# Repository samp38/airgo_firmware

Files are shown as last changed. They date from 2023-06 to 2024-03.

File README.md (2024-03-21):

# airgo_firmware
[link to project](https://wikilab.myhumankit.org/index.php?title=Projets:Automatisation_Support_Joystick_Menton_Fauteuil_Roulant)

## Mode of operation
This setup mean to drive a retractable arm that hold a joystick needed to stir an electrical weelchair. The arm can be retracted/extended to its end positions or stopped inbetween. The system is composed of :
- a push button big enough to be actuated with the head. (temporary contact, normally open)
- an arduino mini pro (atmega328p in its 3.3v version preferably)
- a DC motor H-Bridge driver (DVR 8838) to drive the linear actuator that moves the arm
- the linear actuator itself, with en of course switches that autmatically open the power circuit when the it reaches its end of course positions

Once assembled, the system works as described :
- a long press will retract the arm
- a double press will extend the arm
- a simple press will stop the arm

The system works on 7.4 Li-Ion battery, but the arduino mini pro is powered by one cell only on its RAW input, to shunt the voltage regulator. You also have to remove the led on the arduino, so it won't draw current during deep sleep. With this setup, we're able to draw 5 uA in deep sleep mode. As the arduino mini pro doesn't have a usb2serial chip, you will have to [program it with an external programmer](https://www.instructables.com/How-to-Program-Arduino-Pro-Mini-Using-Arduino-UNO/) (arduino as isp, ftdi...).

## Firmware specifications
- smart push button with actions linked to different press types (short press, long press and double press)
- deep sleep, wake on external interrupt of the push button
- drive DC motor CW or CCW depending on state
- (optional) motor current monitoring via shunt resistor and avr ADC

## Hardware
- arduino mini pro 8Mhz
- motor driver DVR8838
- [Schematics here](./doc/schematics.pdf)
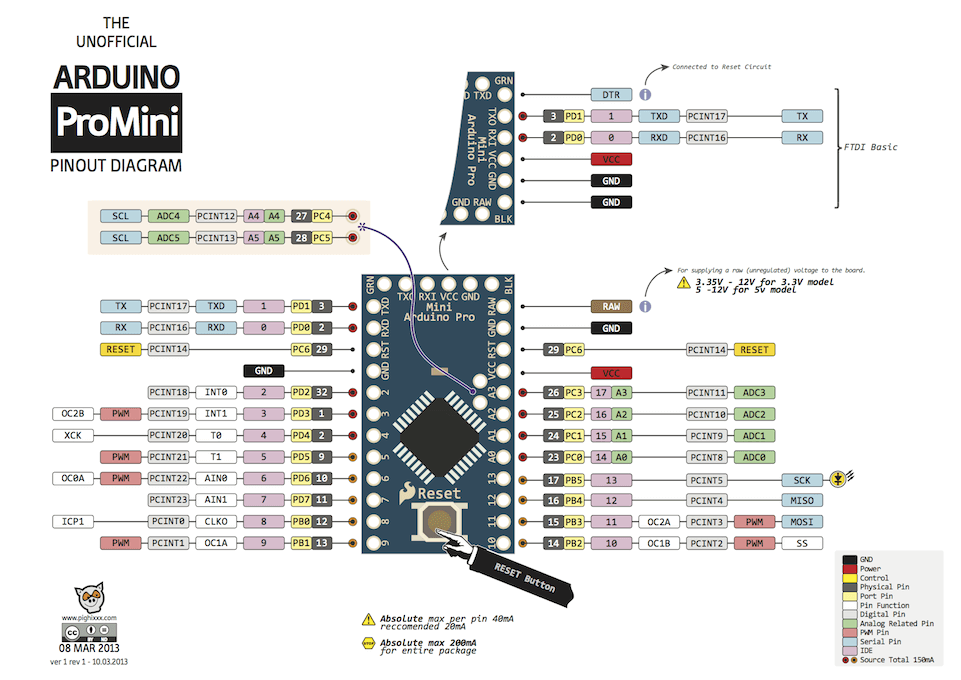
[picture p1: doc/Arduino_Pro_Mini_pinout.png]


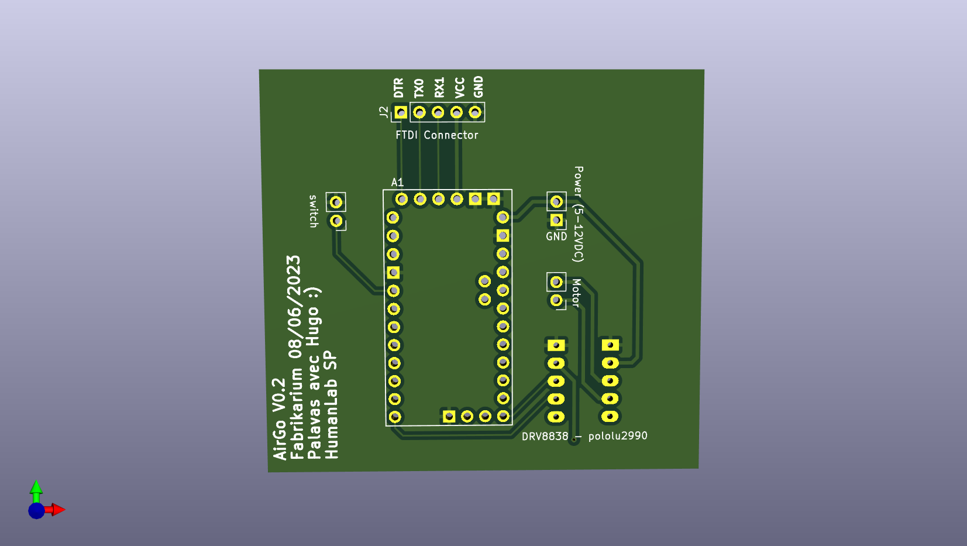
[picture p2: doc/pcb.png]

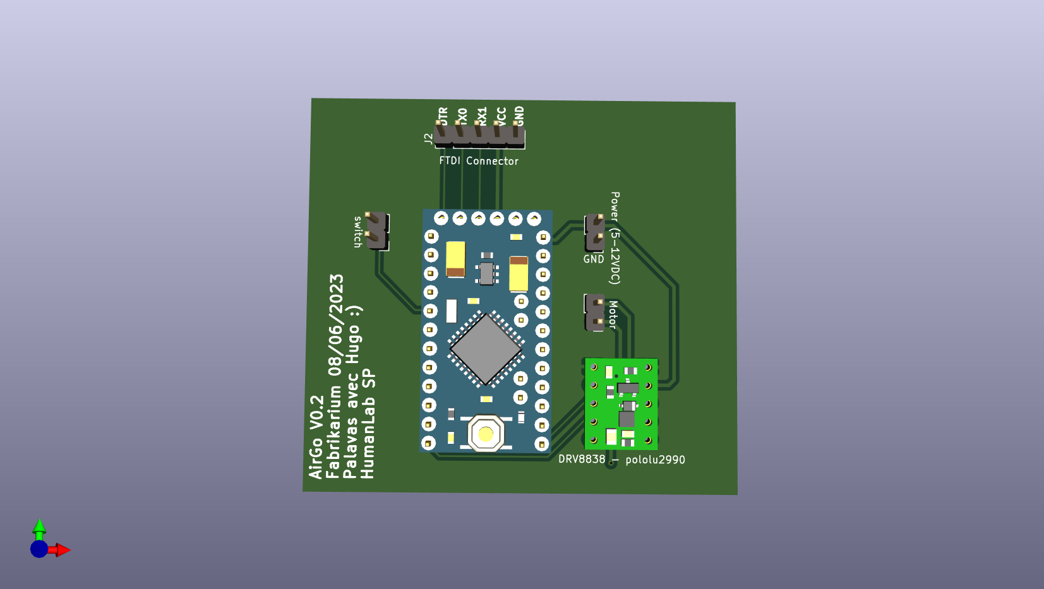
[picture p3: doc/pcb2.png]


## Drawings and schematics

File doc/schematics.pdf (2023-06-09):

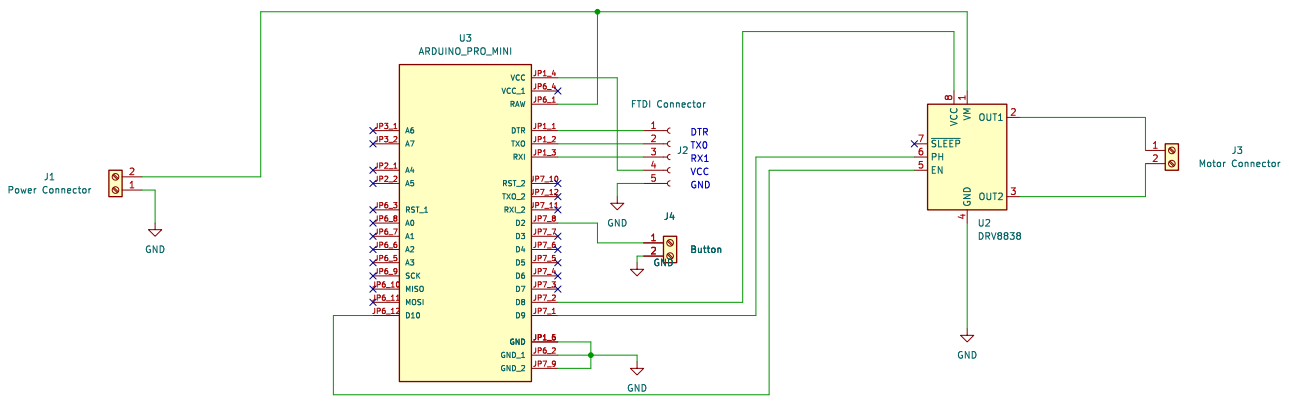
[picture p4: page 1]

J2 FTDI Connector GND GND

4 EN 5 PH 6 ~{SLEEP} 7 VCC

Id: 1/1 Title: File: AirGo.kicad_sch Sheet: /

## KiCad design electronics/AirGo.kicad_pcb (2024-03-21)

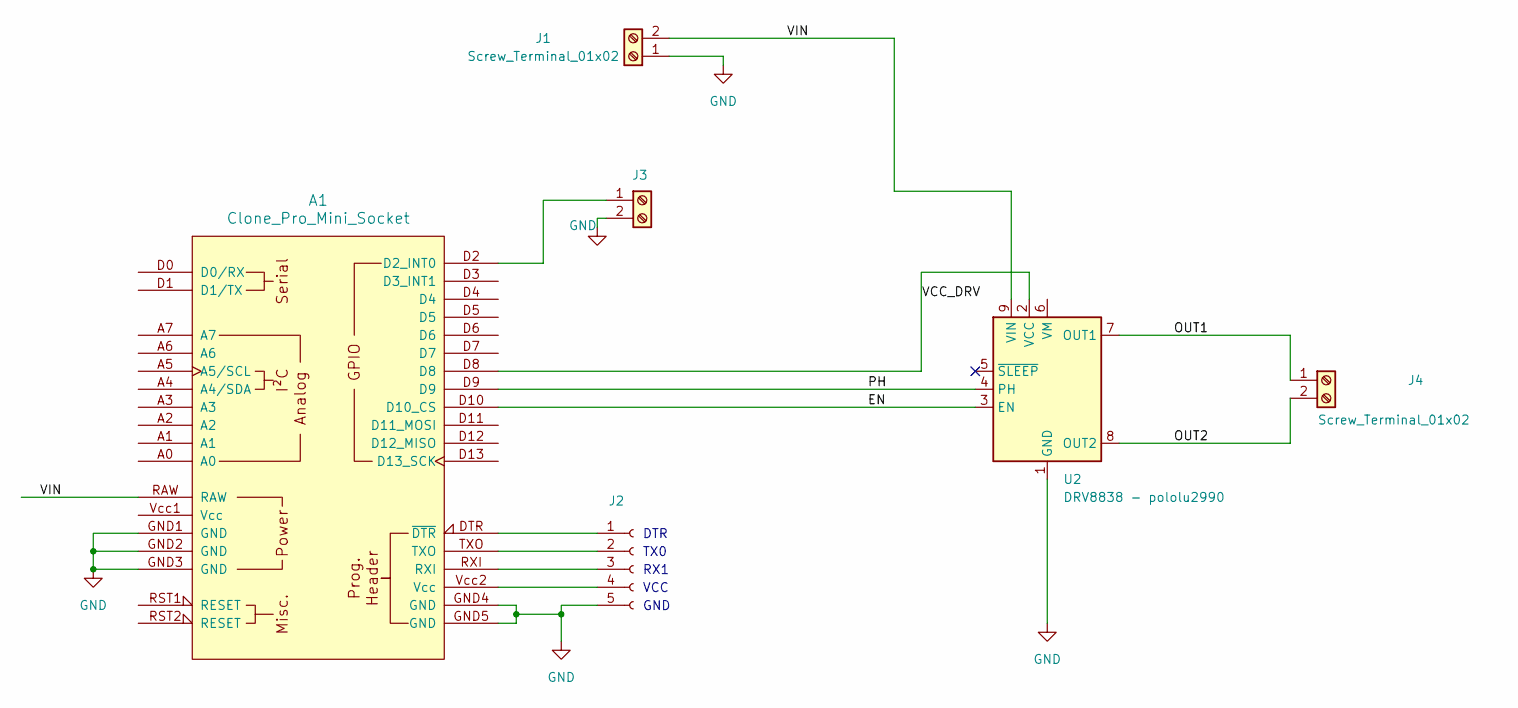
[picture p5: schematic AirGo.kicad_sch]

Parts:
A1: Clone_Pro_Mini_Socket
J1, J3, J4: Screw_Terminal_01x02; PinHeader_1x02_P2.54mm_Vertical
J2: Conn_01x05_Socket; PinHeader_1x05_P2.54mm_Vertical
U2: DRV8838 - pololu2990; DIP-10_W7.62mm_LongPads

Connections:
/EN: A1.D10 (D10_CS), U2.3 (EN)
/OUT1: J4.1, U2.7 (OUT1)
/OUT2: J4.2, U2.8 (OUT2)
/PH: A1.D9, U2.4 (PH)
/VCC_DRV: A1.D8, U2.2 (VCC)
/VIN: A1.RAW, J1.2, U2.9 (VIN)
GND: A1.GND1 (GND), A1.GND2 (GND), A1.GND3 (GND), A1.GND4 (GND), A1.GND5 (GND), J1.1, J2.5, J3.2, U2.1 (GND), U2.10 (GND)
unnamed: A1.D2 (D2_INT0), J3.1
unnamed: A1.DTR (~DTR), J2.1
unnamed: A1.TXO, J2.2
unnamed: A1.RXI, J2.3
unnamed: A1.Vcc2 (Vcc), J2.4

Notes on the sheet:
TX0
DTR
VCC
RX1
GND

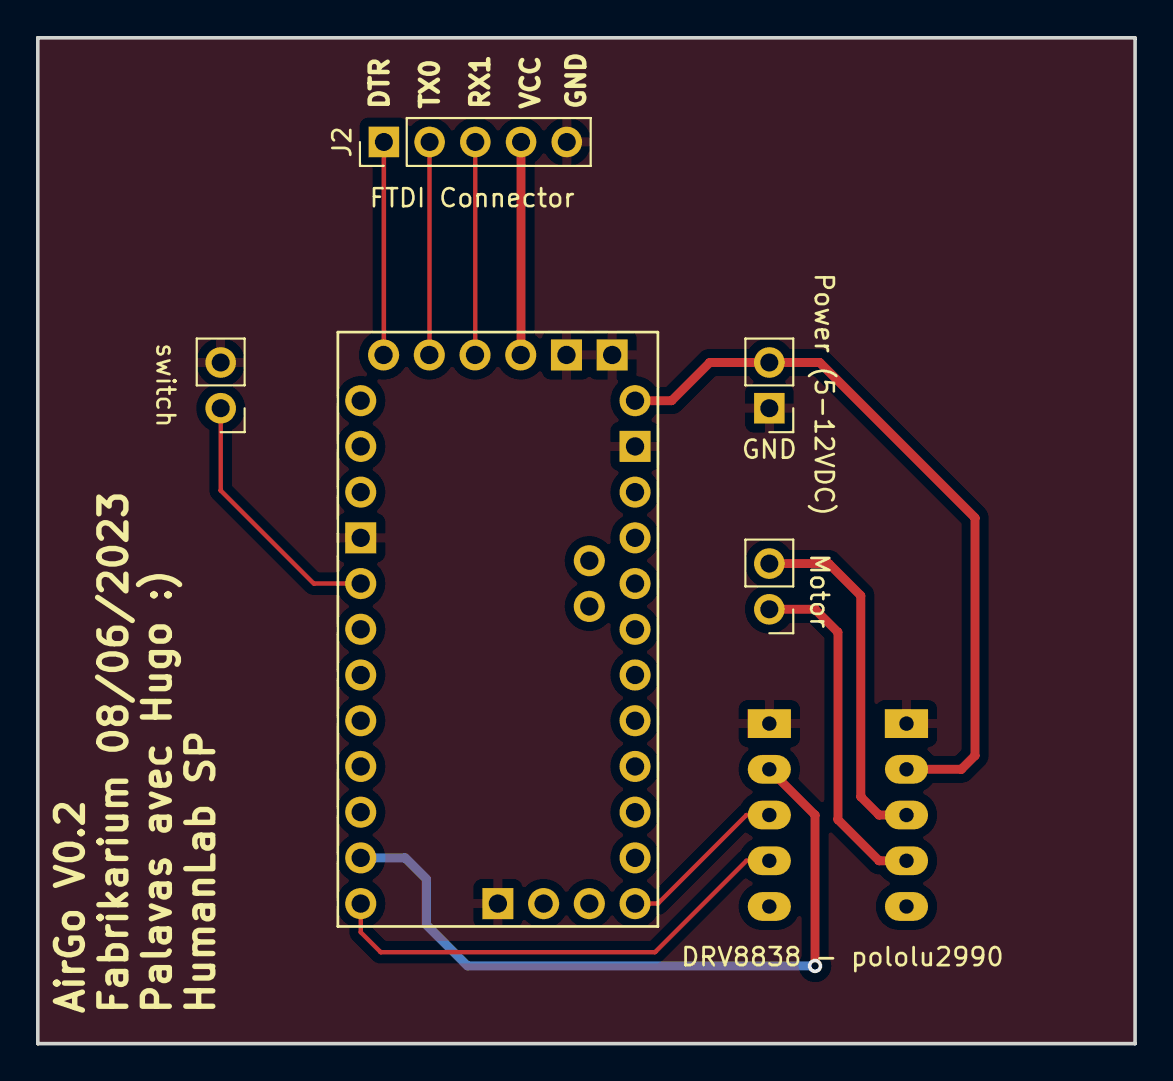
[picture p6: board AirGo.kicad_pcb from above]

Board: 2 copper layers, 61.0 x 55.9 mm, 6 parts (0 on the bottom side), 12 nets.

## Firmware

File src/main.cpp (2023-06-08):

#include "Arduino.h"
#include <EEPROM.h>
#include "bsp.h"
#include "LowPower.h"
#include "OneButton.h"

#define TIMER_SEC 15
#define DOUBLE_CLICK_MS 800
#define LONG_PRESS_MS 1000

// Globals
static volatile bool run_interrupt = 0;
static volatile unsigned int timer_count_sec;
unsigned long pressStartTime;

// Setup a new OneButton on pin PUSH_BUTTON_IN
// The 2. parameter activeLOW is true, because external wiring sets the button to LOW when pressed.
OneButton button(PUSH_BUTTON_IN, true);


void motor_stop() {
    digitalWrite(MOTOR_EN, LOW);
    digitalWrite(MOTOR_DIR, HIGH);
    digitalWrite(MOTOR_DRIVER_PW, LOW);
}

void motor_drive(float speed) {
    unsigned int abs_speed;
    // if speed == 0, stop motor
    if (speed == 0) {
        motor_stop();
        return;
    }

    // if speed is not 0, drive motor
    digitalWrite(MOTOR_DRIVER_PW, HIGH);
    if abs(speed > 100) {
        speed = 100;
    } else if (speed < -100)
    {
        speed = -100;
    }
    
    abs_speed = (unsigned int) (abs(speed) * 255./100.);
    
    if (speed > 0) {
        digitalWrite(MOTOR_DIR, HIGH);
    }
    else
    {
        digitalWrite(MOTOR_DIR, LOW);
    }
    analogWrite(MOTOR_EN, abs_speed);
}

void stop_timer() {
    TIMSK1 |= (0 << TOIE1);   // disable timer overflow interrupt
}

void start_timer(volatile unsigned int local_timer_count_sec = TIMER_SEC) {
    TCNT1 = 31250;   // preload timer
    timer_count_sec = local_timer_count_sec;
    TIMSK1 |= (1 << TOIE1);   // enable timer overflow interrupt
}

void trig_interrupt(){
    // run_interrupt = 1;
    button.tick(); // just call tick() to check the state.
}

// this function will be called when the button was pressed 1 time only.
void singleClick() {
    Serial.println("singleClick() detected.");
    start_timer(1);
    motor_drive(0);
} // singleClick

// this function will be called when the button was pressed 2 times in a short timeframe.
void doubleClick() {
    start_timer();
    Serial.println("doubleClick() detected.");
    Serial.println("extending");
    motor_drive(-100);
} // doubleClick

// this function will be called when the button was held down for 1 second or more.
void longPress() {
    start_timer();
    pressStartTime = millis() - LONG_PRESS_MS; // as set in setPressMs()
    // Serial.println("longPress()");
    Serial.println("retracting");
    motor_drive(100);
} // pressStart()


void setup() {
    Serial.begin(9600);
    noInterrupts(); 
    // Set pin modes
    pinMode(MOTOR_DIR, OUTPUT);
    pinMode(MOTOR_EN, OUTPUT);
    pinMode(MOTOR_DRIVER_PW, OUTPUT);
    pinMode(PUSH_BUTTON_IN, INPUT_PULLUP);

    // setup Timer1
    TCCR1A = 0;
    TCCR1B = 0;

    TCNT1 = 31250;   // preload timer
    TCCR1B |= (1 << CS12);    // 256 prescaler
    TIMSK1 |= (1 << TOIE1);   // enable timer overflow interrupt
    stop_timer();
    motor_stop();

    interrupts();   

    // stop motor
    motor_drive(0);

    // Attach interrupt
    attachInterrupt(digitalPinToInterrupt(PUSH_BUTTON_IN), trig_interrupt, FALLING);

    // button mngmt
    // link the xxxclick functions to be called on xxxclick event.
    button.attachClick(singleClick);
    button.attachDoubleClick(doubleClick);

    button.setClickMs(DOUBLE_CLICK_MS);
    button.setPressMs(LONG_PRESS_MS); // that is the time when LongPressStart is called
    button.attachLongPressStart(longPress);
    // button.attachLongPressStop(pressStop);
}

void loop() {
    button.tick();
}

ISR(TIMER1_OVF_vect)        // interrupt service routine every one second
{
    TCNT1 = 31250;   // preload timer
    timer_count_sec --;
    if (timer_count_sec == 0) {
        stop_timer();
        motor_stop();
        Serial.println("TIMER FINISHED, going to sleep");
        Serial.flush();
        LowPower.powerDown(SLEEP_FOREVER, ADC_OFF, BOD_OFF);
    }
}

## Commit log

2023-06-07 add arduino mini pro pinout image
2023-06-07 add motor & eeprom functions
2023-06-07 Add ISR TODO : timer interrupt to change state and current monitoring
2023-06-08 new motor logic + oneButton implementation
2023-06-08 change motor pins for H Bridge DRV8838
2023-06-08 Update motor routines for DRV8838
2023-06-08 set motor pins mode to output
2023-06-08 stop motor in setup
2023-06-08 stop motor at the end of timer countdown
2023-06-09 add schematics and pcb doc files
2023-06-09 Add Yoann's electronic design
    [AirGo-B_Cu.gbr, AirGo-B_Mask.gbr, AirGo-B_Paste.gbr, AirGo-B_Silkscreen.gbr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]
2024-03-21 Fix pcb (edited with Kicad 8.0) and generate gerber & drill files
    [AirGo-B_Cu.gbr, AirGo-B_Mask.gbr, AirGo-B_Silkscreen.gbr, AirGo-Edge_Cuts.gbr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]
2024-03-21 Add pcb 3d view with th components
